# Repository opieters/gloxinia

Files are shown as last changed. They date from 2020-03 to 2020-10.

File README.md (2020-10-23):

Gloxinia
========

Open-source release of code and PCB-design files of the Gloxinia platform.

Building the code requires MPLAB X 1.35 or above and KiCAD 5.0.2 or above. 

Citing
------

If you use this code for a scientific publication, please consider citing our paper [_Gloxinia—An Open-Source Sensing Platform to Monitor the Dynamic Responses of Plants_](https://doi.org/10.3390/s20113055).

Licence
-------

GNU GPLv3 4.0

A copy of the licence can be found in `LICENCE`.

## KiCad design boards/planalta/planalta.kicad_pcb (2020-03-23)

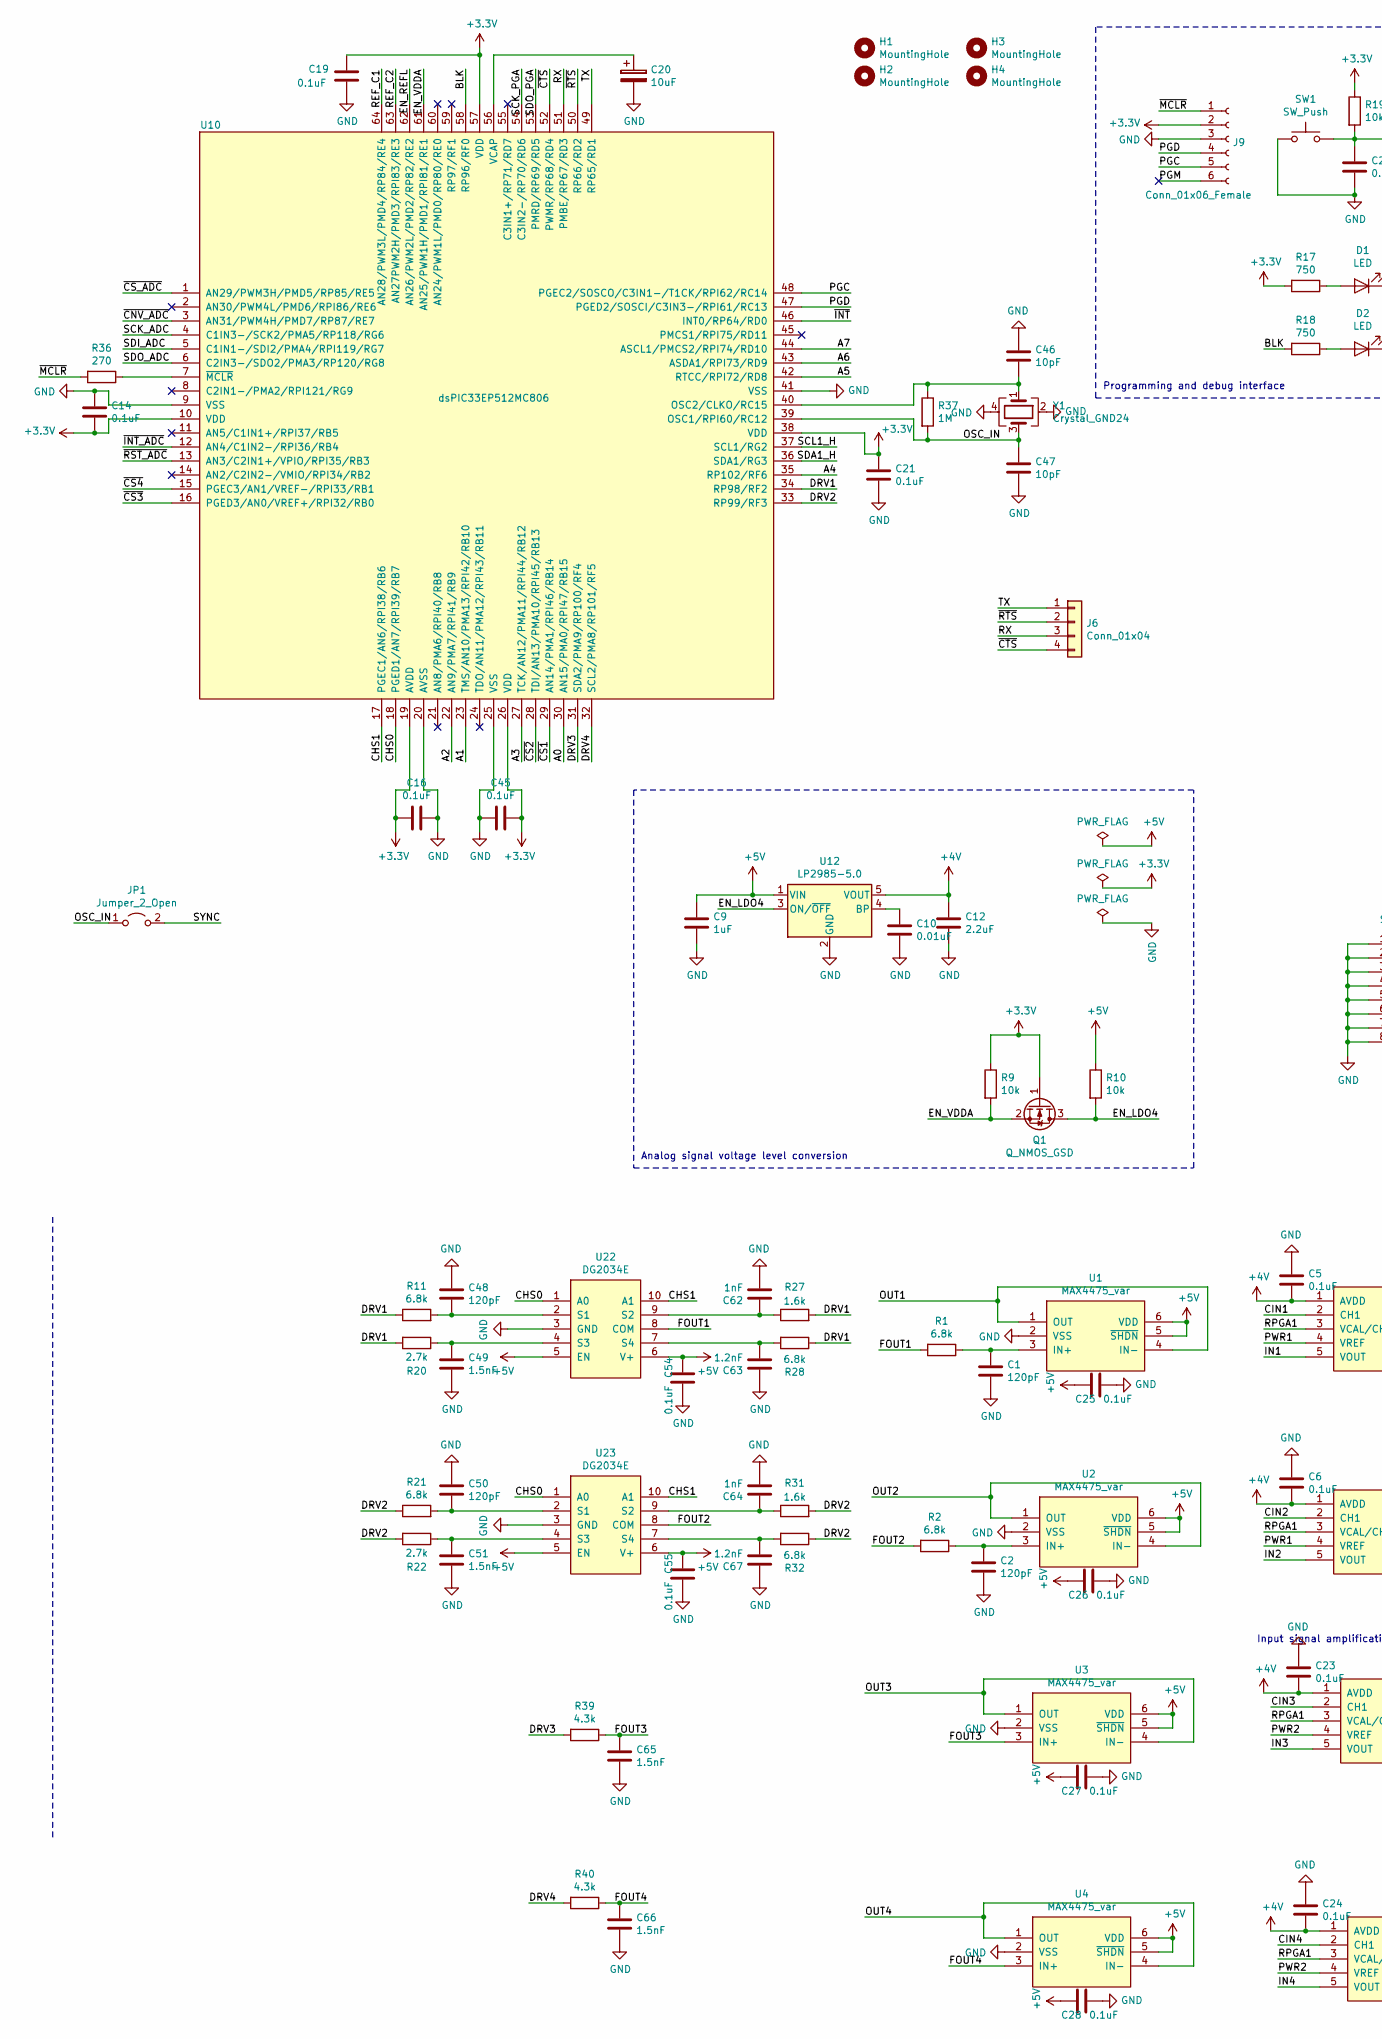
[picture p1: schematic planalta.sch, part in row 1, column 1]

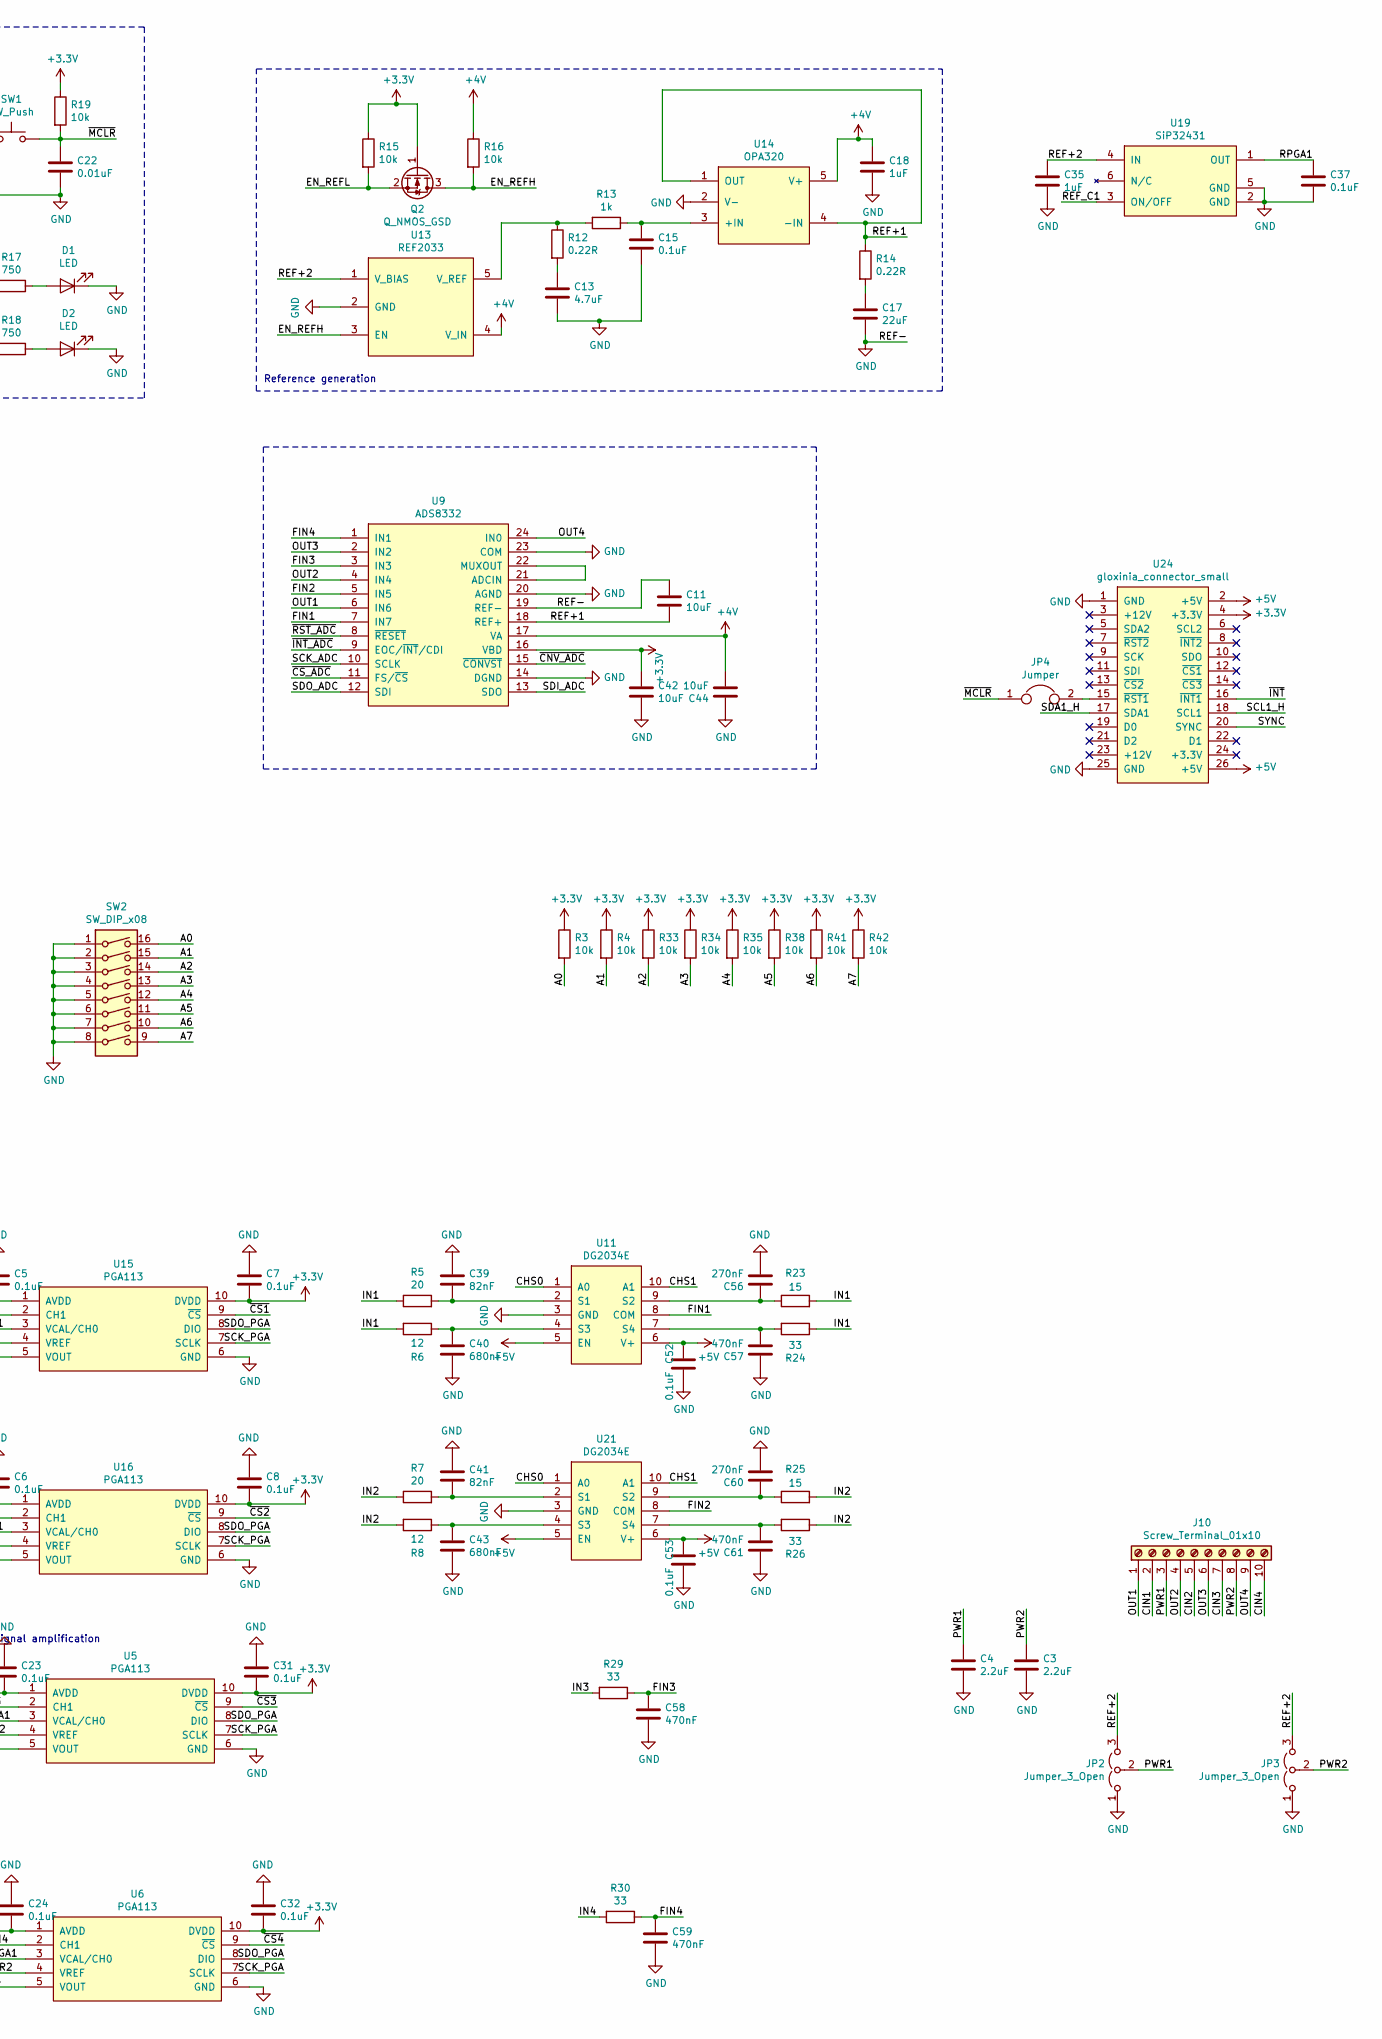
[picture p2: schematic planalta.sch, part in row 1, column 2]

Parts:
C1, C2, C48, C50: 120pF; C_0603_1608Metric; Mouser 80-C0603C121J5GAC
C3, C4, C12: 2.2uF; C_1206_3216Metric; Mouser 791-1206X225K250CT
C5, C6, C7, C8, C14, C15, C16, C19, C21, C23, C24, C25, C26, C27, C28, C31, C32, C37, C45, C52, C53, C54, C55: 0.1uF; C_0603_1608Metric; Mouser 710-885012206071
C9, C18, C35: 1uF; C_0603_1608Metric; Mouser 81-GCM188R71C105K64D
C10, C22: 0.01uF; C_0603_1608Metric; Mouser 81-GRM033C81E103KE4E
C11, C20, C42, C44: 10uF; C_1210_3225Metric; Mouser 963-TMK325BJ106KM-P
C13: 4.7uF; C_1206_3216Metric; Mouser 81-GCG31CR71E475JA1L
C17: 22uF; C_1206_3216Metric; Mouser 963-TMK316BBJ226ML-T
C39, C41: 82nF; C_0603_1608Metric; Mouser 80-C0603C823J3R
C40, C43: 680nF; C_0603_1608Metric; Mouser 710-885012206051
C46, C47: 10pF; C_0603_1608Metric; Mouser 603-CC603FRNPO9BN100
C49, C51, C65, C66: 1.5nF; C_0603_1608Metric; Mouser 710-885012206035
C56, C60: 270nF; C_0603_1608Metric; Mouser 80-C0603C274K8P
C57, C58, C59, C61: 470nF; C_0603_1608Metric; Mouser 710-885012206075
C62, C64: 1nF; C_0603_1608Metric; Mouser 963-TMK325B7105KD-T
C63, C67: 1.2nF; C_0603_1608Metric; Mouser 81-GRM1885C1H122JA01
D1, D2: LED; LED_0603_1608Metric; Mouser 78-TLMS1000
H1, H2, H3, H4: MountingHole; MountingHole_3.2mm_M3
J6: Conn_01x04; PinHeader_1x04_P2.54mm_Vertical
J9: Conn_01x06_Female; PinSocket_1x06_P2.54mm_Vertical
J10: Screw_Terminal_01x10; Header-P5.00mm-10C; Mouser TB003-500-P10BE
JP1: Jumper_2_Open; SolderJumper-2_P1.3mm_Open_Pad1.0x1.5mm
JP2, JP3: Jumper_3_Open; SolderJumper-3_P1.3mm_Open_RoundedPad1.0x1.5mm
JP4: Jumper; SolderJumper-2_P1.3mm_Open_RoundedPad1.0x1.5mm
Q1, Q2: Q_NMOS_GSD; SOT-23; Mouser 512-BSS138
R1, R2, R11, R21, R28, R32: 6.8k; R_0603_1608Metric; Mouser 667-ERJ-3RBD6801V
R3, R4, R9, R10, R15, R16, R19, R33, R34, R35, R38, R41, R42: 10k; R_0603_1608Metric; Mouser 284-APC0603B10K0N
R5, R7: 20; R_0603_1608Metric; Mouser 71-CRCW060320R0FKEAC
R6, R8: 12; R_0603_1608Metric; Mouser 667-ERJ-3EKF15R0V
R12, R14: 0.22R; R_0603_1608Metric; Mouser 667-ERJ-3RQFR22V
R13: 1k; R_0603_1608Metric; Mouser 652-CR0603-FX1001HLF
R17, R18: 750; R_0603_1608Metric; Mouser 603-RC0603FR-07750RL
R20, R22: 2.7k; R_0603_1608Metric; Mouser 603-AC0603FR-102K7L
R23, R25: 15; R_0603_1608Metric; Mouser 667-ERJ-3EKF15R0V
R24, R26, R29, R30: 33; R_0603_1608Metric; Mouser 71-CRCW060333R0FKEAC
R27, R31: 1.6k; R_0603_1608Metric; Mouser 603-RC0603FR-071K6L
R36: 270; R_0603_1608Metric; Mouser 603-RC0603FR-07270RL
R37: 1M; R_0603_1608Metric; Mouser 603-RC0603FR-101ML
R39, R40: 4.3k; R_0603_1608Metric
SW1: SW_Push; SW_SPST_KMR2; Mouser 611-KMR621NGLFS
SW2: SW_DIP_x08; SW_DIP_SPSTx08_Slide_Omron_A6H-8101_W6.15mm_P1.27mm; Mouser 653-A6H-8101
U1, U2, U3, U4: MAX4475_var; SOT-23-6; Mouser 700-MAX4475AUT+T
U5, U6, U15, U16: PGA113; MSOP-10_3x3mm_P0.5mm; Mouser 595-PGA113AIDGSR
U9: ADS8332; TSSOP-24_4.4x7.8mm_P0.65mm; Mouser 595-ADS8332IBPWR
U10: dsPIC33EP512MC806; TQFP-64_10x10mm_P0.5mm; Mouser 579-33EP512MC806IPT
U11, U21, U22, U23: DG2034E; MSOP-10_3x3mm_P0.5mm; Mouser 78-DG2034EDQ-T1-GE3
U12: LP2985-5.0; SOT-23-5; Mouser 926-LP2985IM540NOPB
U13: REF2033; SOT-23-5; Mouser 595-REF2033AIDDCR
U14: OPA320; SOT-23-5; Mouser 595-OPA320AIDBVR
U19: SiP32431; SOT-363_SC-70-6; Mouser 781-SIP32431DR3-GE3
U24: gloxinia_connector_small; PinHeader_2x13_P2.54mm_Vertical; Mouser 200-SSQ11303TD
Y1: Crystal_GND24; Crystal_SMD_Abracon_ABM3B-4Pin_5.0x3.2mm; Mouser 520-80-10-30B-CWNT

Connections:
+3V3: C7.2, C8.2, C14.2, C16.2, C19.1, C21.1, C31.2, C32.2, C42.1, C45.1, J9.2, Q1.1 (G), Q2.1 (G), R3.1, R4.1, R9.1, R15.1, R17.2, R19.1, R33.1, R34.1, R35.1, R38.1, R41.1, R42.1, U5.10 (DVDD), U6.10 (DVDD), U9.16 (VBD), U10.10 (VDD), U10.19 (AVDD), U10.26 (VDD), U10.38 (VDD), U10.57 (VDD), U15.10 (DVDD), U16.10 (DVDD), U24.4 (+3.3V)
+4V: C5.2, C6.2, C12.1, C18.1, C23.2, C24.2, C44.2, R16.1, U5.1 (AVDD), U6.1 (AVDD), U9.17 (VA), U12.5 (VOUT), U13.4 (V_IN), U14.5 (V+), U15.1 (AVDD), U16.1 (AVDD)
+5V: C9.1, C25.2, C26.2, C27.2, C28.2, C52.2, C53.2, C54.2, C55.2, R10.1, U1.5 (~SHDN), U1.6 (VDD), U2.5 (~SHDN), U2.6 (VDD), U3.5 (~SHDN), U3.6 (VDD), U4.5 (~SHDN), U4.6 (VDD), U11.5 (EN), U11.6 (V+), U12.1 (VIN), U21.5 (EN), U21.6 (V+), U22.5 (EN), U22.6 (V+), U23.5 (EN), U23.6 (V+), U24.2 (+5V), U24.26 (+5V)
/A0: R3.2, SW2.16, U10.30 (AN15/PMA0/RPI47/RB15)
/A1: R4.2, SW2.15, U10.23 (TMS/AN10/PMA13/RPI42/RB10)
/A2: R33.2, SW2.14, U10.22 (AN9/PMA7/RPI41/RB9)
/A3: R34.2, SW2.13, U10.27 (TCK/AN12/PMA11/RPI44/RB12)
/A4: R35.2, SW2.12, U10.35 (RP102/RF6)
/A5: R38.2, SW2.11, U10.42 (RTCC/RPI72/RD8)
/A6: R41.2, SW2.10, U10.43 (ASDA1/RPI73/RD9)
/A7: R42.2, SW2.9, U10.44 (ASCL1/PMCS2/RPI74/RD10)
/BLK: R18.2, U10.58 (RP96/RF0)
/CHS0: U10.18 (PGED1/AN7/RPI39/RB7), U11.1 (A0), U21.1 (A0), U22.1 (A0), U23.1 (A0)
/CHS1: U10.17 (PGEC1/AN6/RPI38/RB6), U11.10 (A1), U21.10 (A1), U22.10 (A1), U23.10 (A1)
/CIN1: J10.2, U15.2 (CH1)
/CIN2: J10.5, U16.2 (CH1)
/CIN3: J10.7, U5.2 (CH1)
/CIN4: J10.10, U6.2 (CH1)
/DRV1: R11.1, R20.2, R27.2, R28.1, U10.34 (RP98/RF2)
/DRV2: R21.1, R22.2, R31.2, R32.1, U10.33 (RP99/RF3)
/DRV3: R39.2, U10.31 (SDA2/PMA9/RP100/RF4)
/DRV4: R40.2, U10.32 (SCL2/PMA8/RP101/RF5)
/EN_LDO4: Q1.3 (D), R10.2, U12.3 (ON/~OFF~)
/EN_REFH: Q2.3 (D), R16.2, U13.3 (EN)
/EN_REFL: Q2.2 (S), R15.2, U10.62 (AN26/PWM2L/PMD2/RP82/RE2)
/EN_VDDA: Q1.2 (S), R9.2, U10.61 (AN25/PWM1H/PMD1/RPI81/RE1)
/FIN1: U9.7 (IN7), U11.8 (COM)
/FIN2: U9.5 (IN5), U21.8 (COM)
/FIN3: C58.1, R29.1, U9.3 (IN3)
/FIN4: C59.1, R30.1, U9.1 (IN1)
/FOUT1: R1.2, U22.8 (COM)
/FOUT2: R2.2, U23.8 (COM)
/FOUT3: C65.1, R39.1, U3.3 (IN+)
/FOUT4: C66.1, R40.1, U4.3 (IN+)
/IN1: R5.1, R6.2, R23.2, R24.1, U15.5 (VOUT)
/IN2: R7.1, R8.2, R25.2, R26.1, U16.5 (VOUT)
/IN3: R29.2, U5.5 (VOUT)
/IN4: R30.2, U6.5 (VOUT)
/OSC_IN: C47.1, JP1.1 (A), R37.2, U10.39 (OSC1/RPI60/RC12), Y1.3
/OUT1: J10.1, U1.1 (OUT), U1.4 (IN-), U9.6 (IN6)
/OUT2: J10.4, U2.1 (OUT), U2.4 (IN-), U9.4 (IN4)
/OUT3: J10.6, U3.1 (OUT), U3.4 (IN-), U9.2 (IN2)
/OUT4: J10.9, U4.1 (OUT), U4.4 (IN-), U9.24 (IN0)
/PGC: J9.5, U10.48 (PGEC2/SOSCO/C3IN1-/T1CK/RPI62/RC14)
/PGD: J9.4, U10.47 (PGED2/SOSCI/C3IN3-/RPI61/RC13)
/PGM: J9.6
/PWR1: C4.1, J10.3, JP2.2 (C), U15.4 (VREF), U16.4 (VREF)
/PWR2: C3.1, J10.8, JP3.2 (C), U5.4 (VREF), U6.4 (VREF)
/REF+1: C11.2, R14.1, U9.18 (REF+), U14.1 (OUT), U14.4 (-IN)
/REF+2: C35.1, JP2.3 (B), JP3.3 (B), U13.1 (V_BIAS), U19.4 (IN)
/REF_C1: U10.64 (AN28/PWM3L/PMD4/RP84/RE4), U19.3 (ON/OFF)
/REF_C2: U10.63 (AN27PWM2H/PMD3/RPI83/RE3)
/RPGA1: C37.1, U5.3 (VCAL/CH0), U6.3 (VCAL/CH0), U15.3 (VCAL/CH0), U16.3 (VCAL/CH0), U19.1 (OUT)
/RX: J6.3, U10.51 (PMBE/RP67/RD3)
/SCK_ADC: U9.10 (SCLK), U10.4 (C1IN3-/SCK2/PMA5/RP118/RG6)
/SCK_PGA: U5.7 (SCLK), U6.7 (SCLK), U10.54 (C3IN2-/RP70/RD6), U15.7 (SCLK), U16.7 (SCLK)
/SCL1_H: U10.37 (SCL1/RG2), U24.18 (SCL1)
/SDA1_H: U10.36 (SDA1/RG3), U24.17 (SDA1)
/SDI_ADC: U9.13 (SDO), U10.5 (C1IN1-/SDI2/PMA4/RPI119/RG7)
/SDO_ADC: U9.12 (SDI), U10.6 (C2IN3-/SDO2/PMA3/RP120/RG8)
/SDO_PGA: U5.8 (DIO), U6.8 (DIO), U10.53 (PMRD/RP69/RD5), U15.8 (DIO), U16.8 (DIO)
/SYNC: JP1.2 (B), U24.20 (SYNC)
/TX: J6.1, U10.49 (RP65/RD1)
/~CNV_ADC: U9.15 (~CONVST), U10.3 (AN31/PWM4H/PMD7/RP87/RE7)
/~CS1: U10.29 (AN14/PMA1/RPI46/RB14), U15.9 (~CS)
/~CS2: U10.28 (TDI/AN13/PMA10/RPI45/RB13), U16.9 (~CS)
/~CS3: U5.9 (~CS), U10.16 (PGED3/AN0/VREF+/RPI32/RB0)
/~CS4: U6.9 (~CS), U10.15 (PGEC3/AN1/VREF-/RPI33/RB1)
/~CS_ADC: U9.11 (FS/~CS), U10.1 (AN29/PWM3H/PMD5/RP85/RE5)
/~CTS: J6.4, U10.52 (PWMR/RP68/RD4)
/~INT: U10.46 (INT0/RP64/RD0), U24.16 (~INT1)
/~INT_ADC: U9.9 (EOC/~INT~/CDI), U10.12 (AN4/C1IN2-/RPI36/RB4)
/~MCLR: C22.1, J9.1, JP4.1, R19.2, R36.2, SW1.2
/~RST_ADC: U9.8 (~RESET), U10.13 (AN3/C2IN1+/VPIO/RPI35/RB3)
/~RTS: J6.2, U10.50 (RP66/RD2)
GND: C1.2, C2.2, C3.2, C4.2, C5.1, C6.1, C7.1, C8.1, C9.2, C10.2, C11.1, C12.2, C13.2, C14.1, C15.2, C16.1, C17.2, C18.2, C19.2, C20.2, C21.2, C22.2, C23.1, C24.1, C25.1, C26.1, C27.1, C28.1, C31.1, C32.1, C35.2, C37.2, C39.1, C40.2, C41.1, C42.2, C43.2, C44.1, C45.2, C46.1, C47.2, C48.1, C49.2, C50.1, C51.2, C52.1, C53.1, C54.1, C55.1, C56.2, C57.1, C58.2, C59.2, C60.2, C61.1, C62.2, C63.1, C64.2, C65.2, C66.2, C67.1, D1.1 (K), D2.1 (K), J9.3, JP2.1 (A), JP3.1 (A), SW1.1, SW2.1, SW2.2, SW2.3, SW2.4, SW2.5, SW2.6, SW2.7, SW2.8, U1.2 (VSS), U2.2 (VSS), U3.2 (VSS), U4.2 (VSS), U5.6 (GND), U6.6 (GND), U9.14 (DGND), U9.19 (REF-), U9.20 (AGND), U9.23 (COM), U10.9 (VSS), U10.20 (AVSS), U10.25 (VSS), U10.41 (VSS), U11.3 (GND), U12.2 (GND), U13.2 (GND), U14.2 (V-), U15.6 (GND), U16.6 (GND), U19.2 (GND), U19.5 (GND), U21.3 (GND), U22.3 (GND), U23.3 (GND), U24.1 (GND), U24.25 (GND), Y1.2, Y1.4
unnamed: C1.1, R1.1, U1.3 (IN+)
unnamed: C2.1, R2.1, U2.3 (IN+)
unnamed: C10.1, U12.4 (BP)
unnamed: C13.1, R12.2
unnamed: C15.1, R13.1, U14.3 (+IN)
unnamed: C17.1, R14.2
unnamed: C20.1, U10.56 (VCAP)
unnamed: C39.2, R5.2, U11.2 (S1)
unnamed: C40.1, R6.1, U11.4 (S3)
unnamed: C41.2, R7.2, U21.2 (S1)
unnamed: C43.1, R8.1, U21.4 (S3)
unnamed: C46.2, R37.1, U10.40 (OSC2/CLKO/RC15), Y1.1
unnamed: C48.2, R11.2, U22.2 (S1)
unnamed: C49.1, R20.1, U22.4 (S3)
unnamed: C50.2, R21.2, U23.2 (S1)
unnamed: C51.1, R22.1, U23.4 (S3)
unnamed: C56.1, R23.1, U11.9 (S2)
unnamed: C57.2, R24.2, U11.7 (S4)
unnamed: C60.1, R25.1, U21.9 (S2)
unnamed: C61.2, R26.2, U21.7 (S4)
unnamed: C62.1, R27.1, U22.9 (S2)
unnamed: C63.2, R28.2, U22.7 (S4)
unnamed: C64.1, R31.1, U23.9 (S2)
unnamed: C67.2, R32.2, U23.7 (S4)
unnamed: D1.2 (A), R17.1
unnamed: D2.2 (A), R18.1
unnamed: JP4.2, U24.15 (~RST1)
unnamed: R12.1, R13.2, U13.5 (V_REF)
unnamed: R36.1, U10.7 (~MCLR)
unnamed: U9.21 (ADCIN), U9.22 (MUXOUT)

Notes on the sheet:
Programming and debug interface
Reference generation
Analog signal voltage level conversion
Input signal amplification

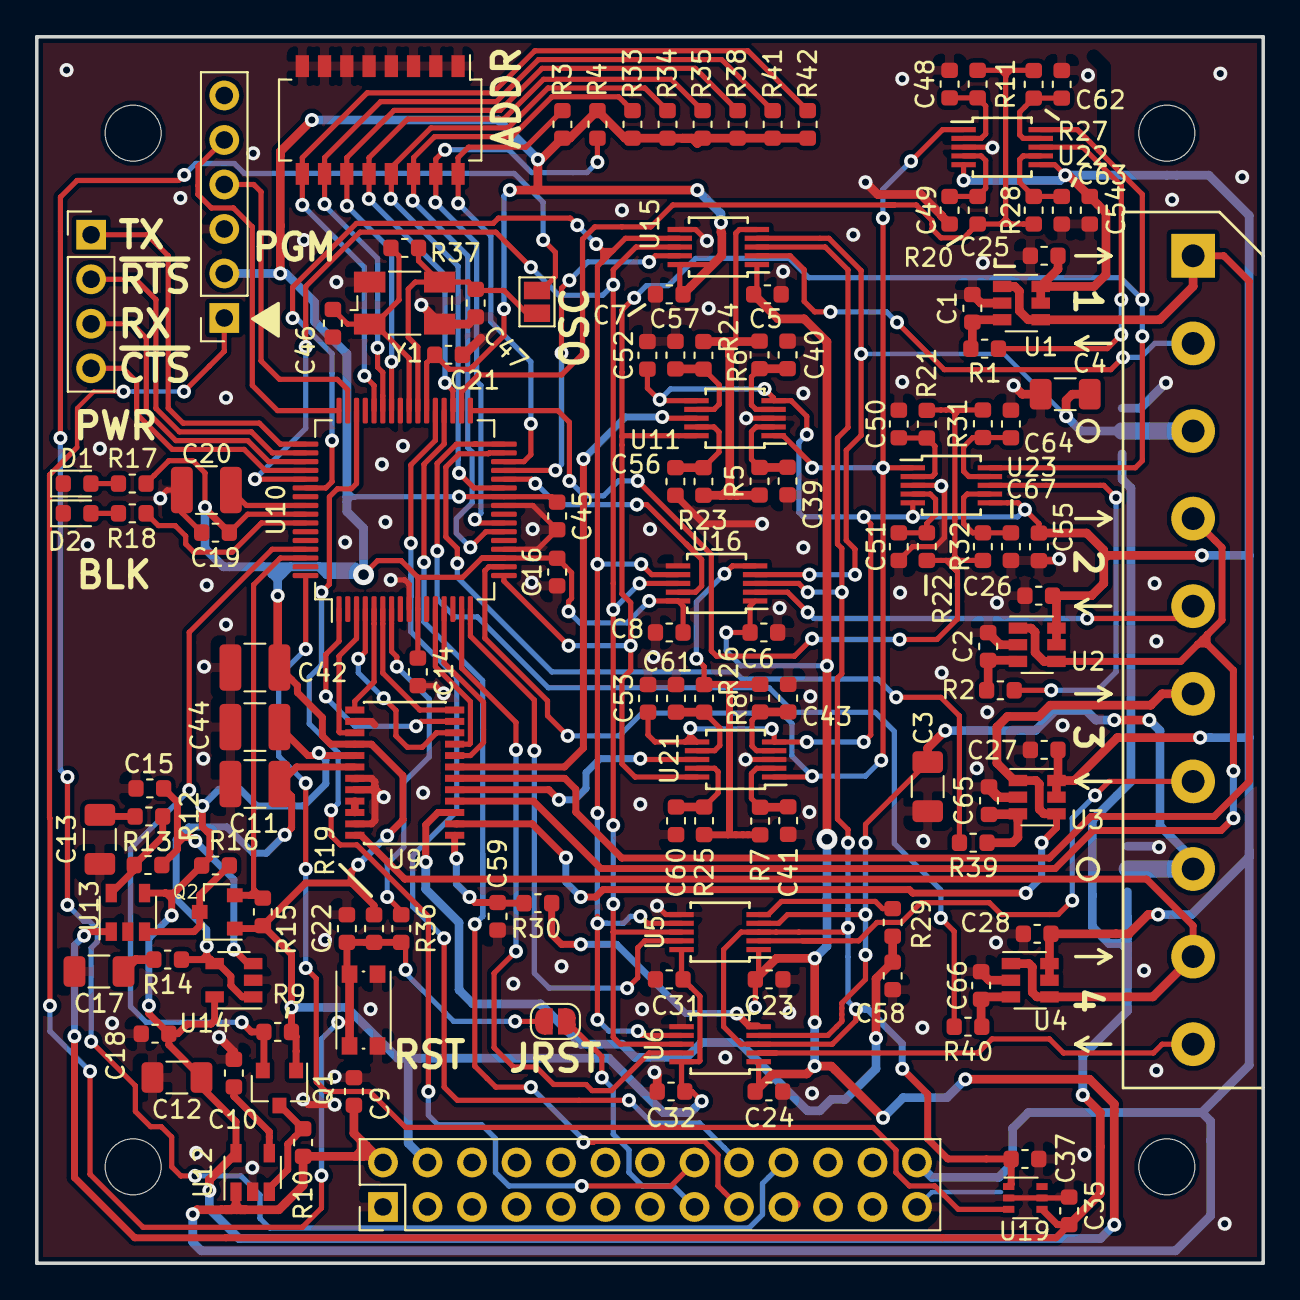
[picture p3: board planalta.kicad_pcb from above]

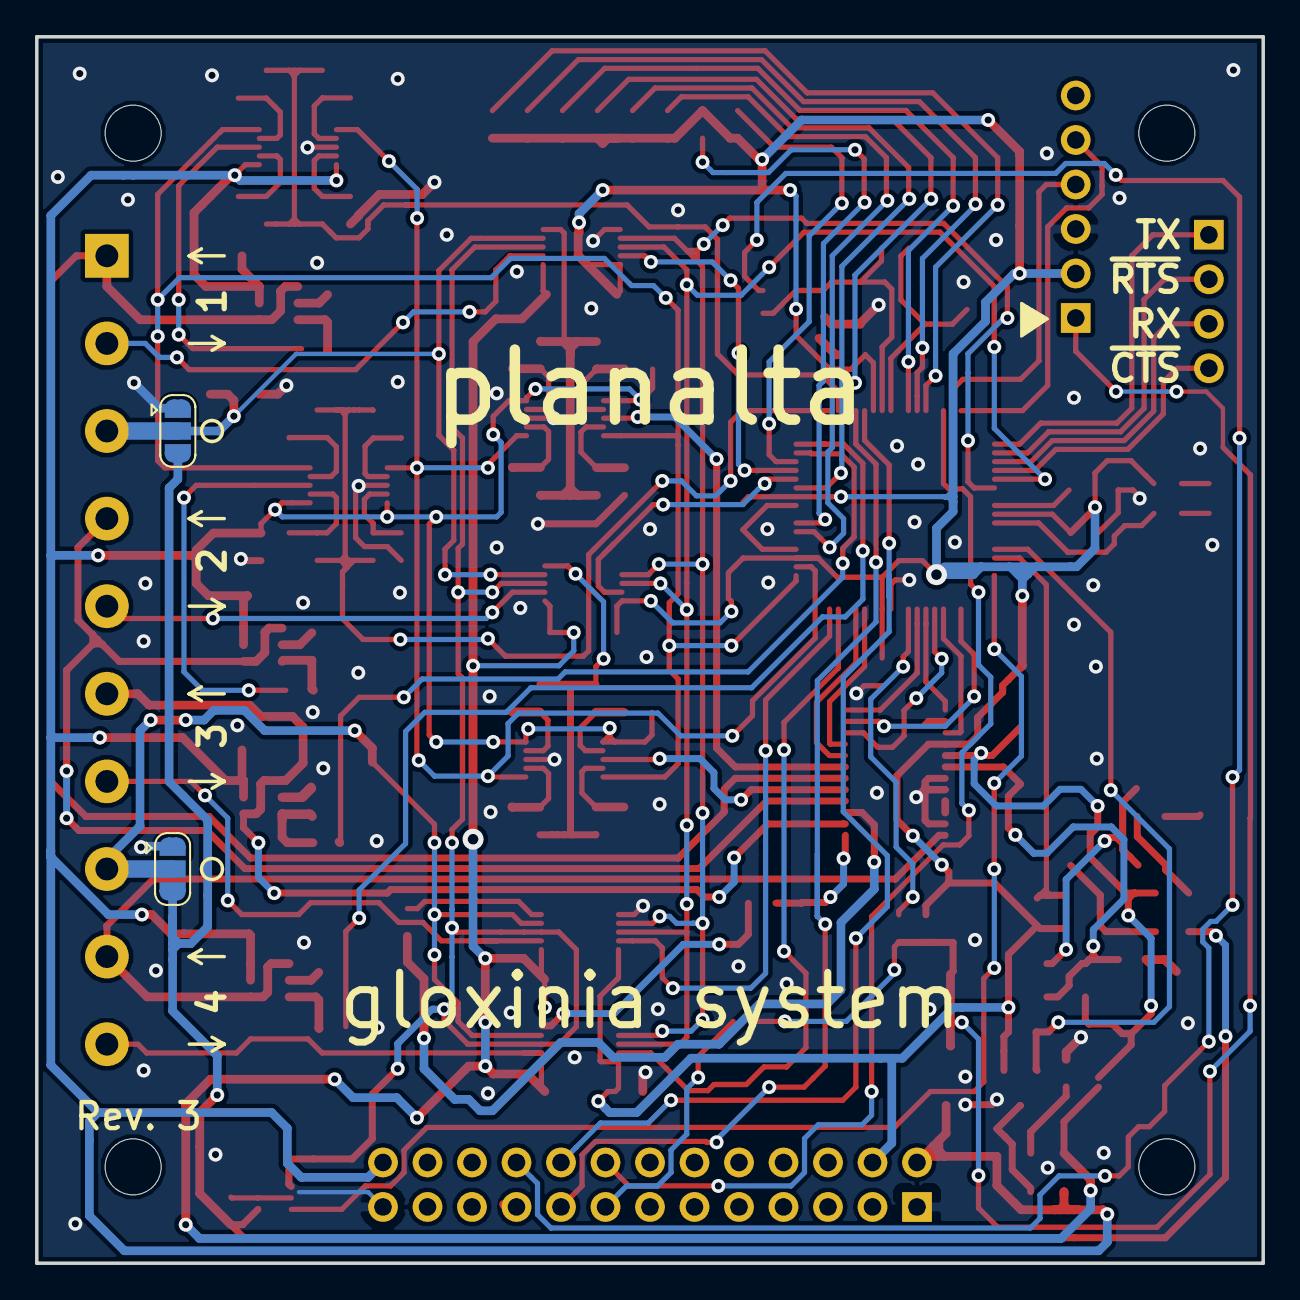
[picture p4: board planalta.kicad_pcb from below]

Board: 2 copper layers, 70.0 x 70.0 mm, 140 parts (2 on the bottom side), 104 nets.

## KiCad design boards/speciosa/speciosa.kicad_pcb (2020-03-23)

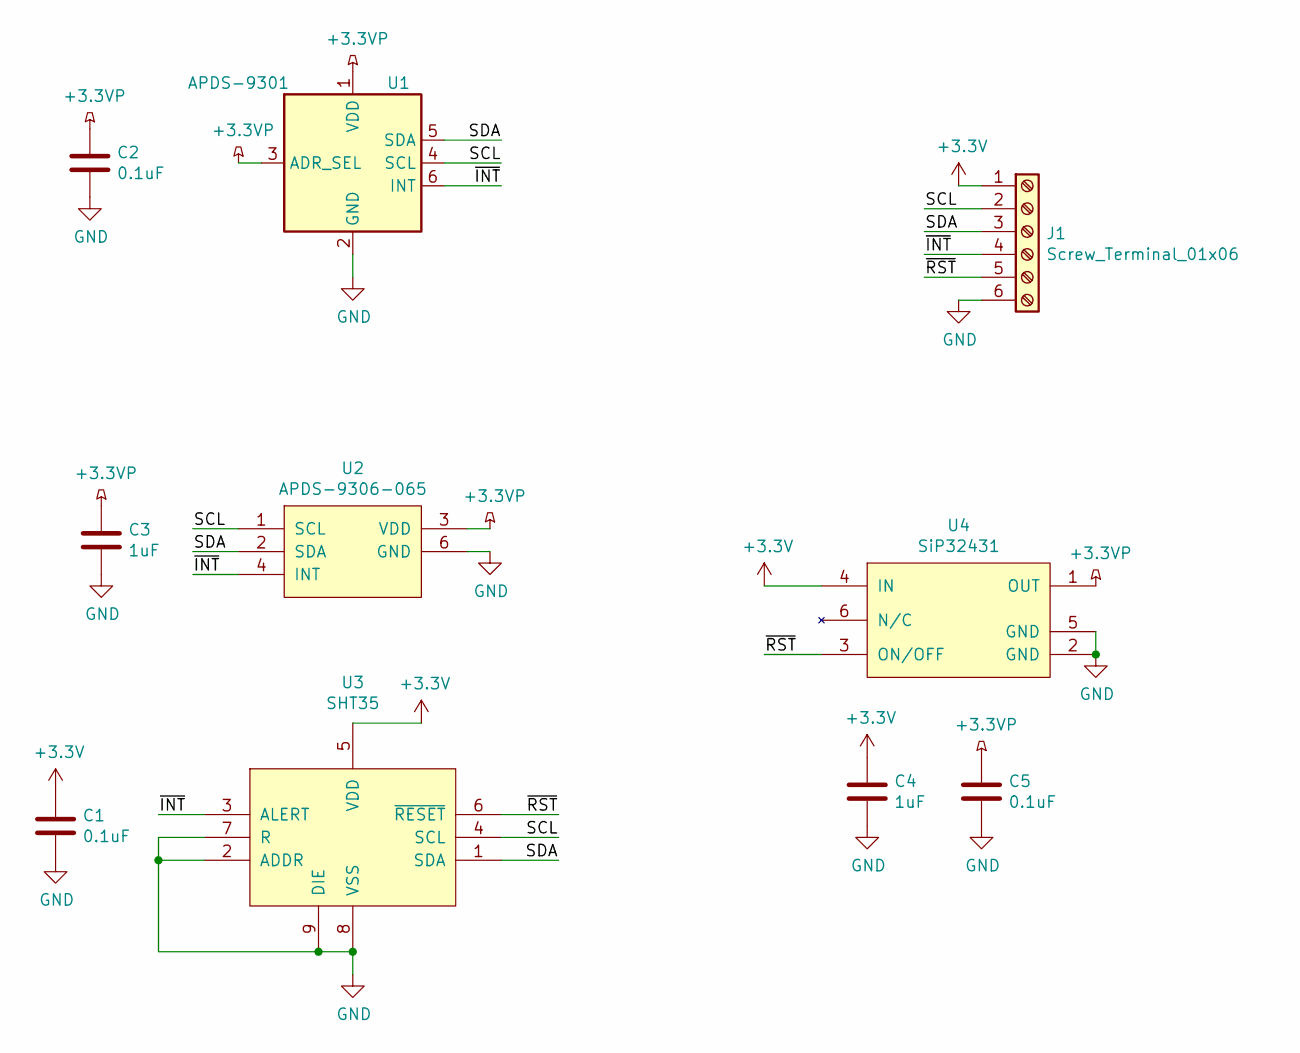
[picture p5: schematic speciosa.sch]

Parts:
C1, C2, C5: 0.1uF; C_0603_1608Metric; Mouser 810-CGA3E2X8R1E104K
C3, C4: 1uF; C_0603_1608Metric; Mouser 710-885012106022
J1: Screw_Terminal_01x06; PinHeader_1x06_P2.54mm_Vertical
U1: APDS-9301; Broadcom_APDS-9301; Farnell 2497389
U2: APDS-9306-065; Mouser 630-APDS-9306-065
U3: SHT35; 8P-1EP-DFN_2.5x2.5; Mouser 403-SHT35-DIS-F
U4: SiP32431; SOT-363_SC-70-6; Mouser 781-SIP32431DR3-GE3

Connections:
+3.3VP: C2.1, C3.1, C5.1, U1.1 (VDD), U1.3 (ADR_SEL), U2.3 (VDD), U4.1 (OUT)
+3V3: C1.1, C4.1, J1.1, U3.5 (VDD), U4.4 (IN)
/SCL: J1.2, U1.4 (SCL), U2.1 (SCL), U3.4 (SCL)
/SDA: J1.3, U1.5 (SDA), U2.2 (SDA), U3.1 (SDA)
/~INT: J1.4, U1.6 (INT), U2.4 (INT), U3.3 (ALERT)
/~RST: J1.5, U3.6 (~RESET), U4.3 (ON/OFF)
GND: C1.2, C2.2, C3.2, C4.2, C5.2, J1.6, U1.2 (GND), U2.6 (GND), U3.2 (ADDR), U3.7 (R), U3.8 (VSS), U3.9 (DIE), U4.2 (GND), U4.5 (GND)

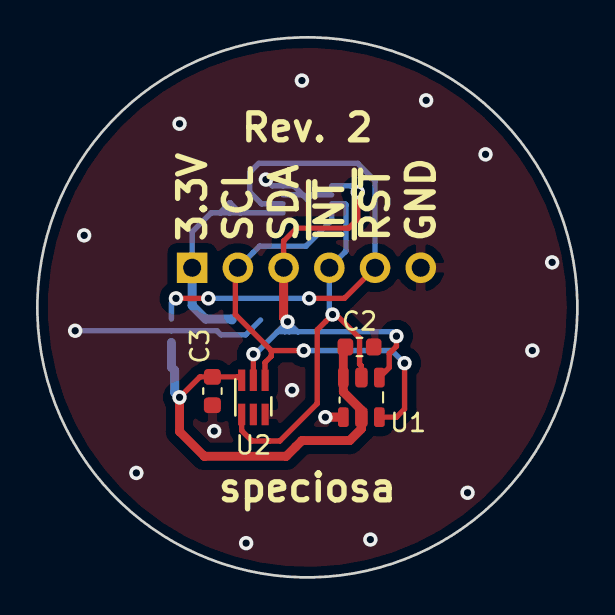
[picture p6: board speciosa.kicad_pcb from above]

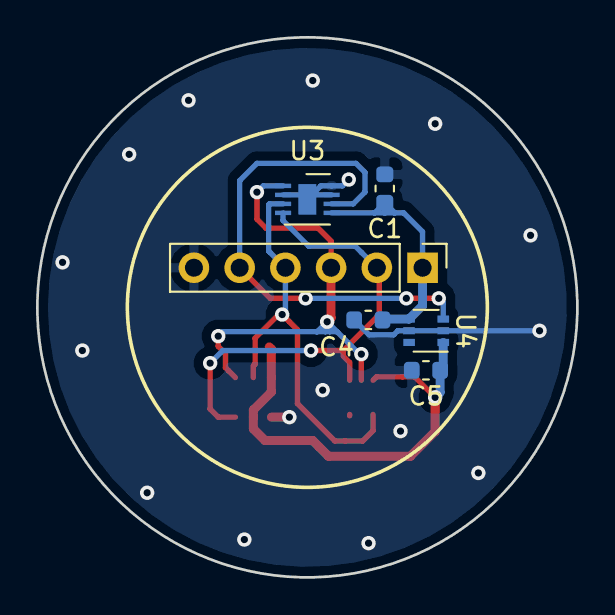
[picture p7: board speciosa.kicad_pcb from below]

Board: 2 copper layers, 30.0 x 30.0 mm, 10 parts (6 on the bottom side), 7 nets.

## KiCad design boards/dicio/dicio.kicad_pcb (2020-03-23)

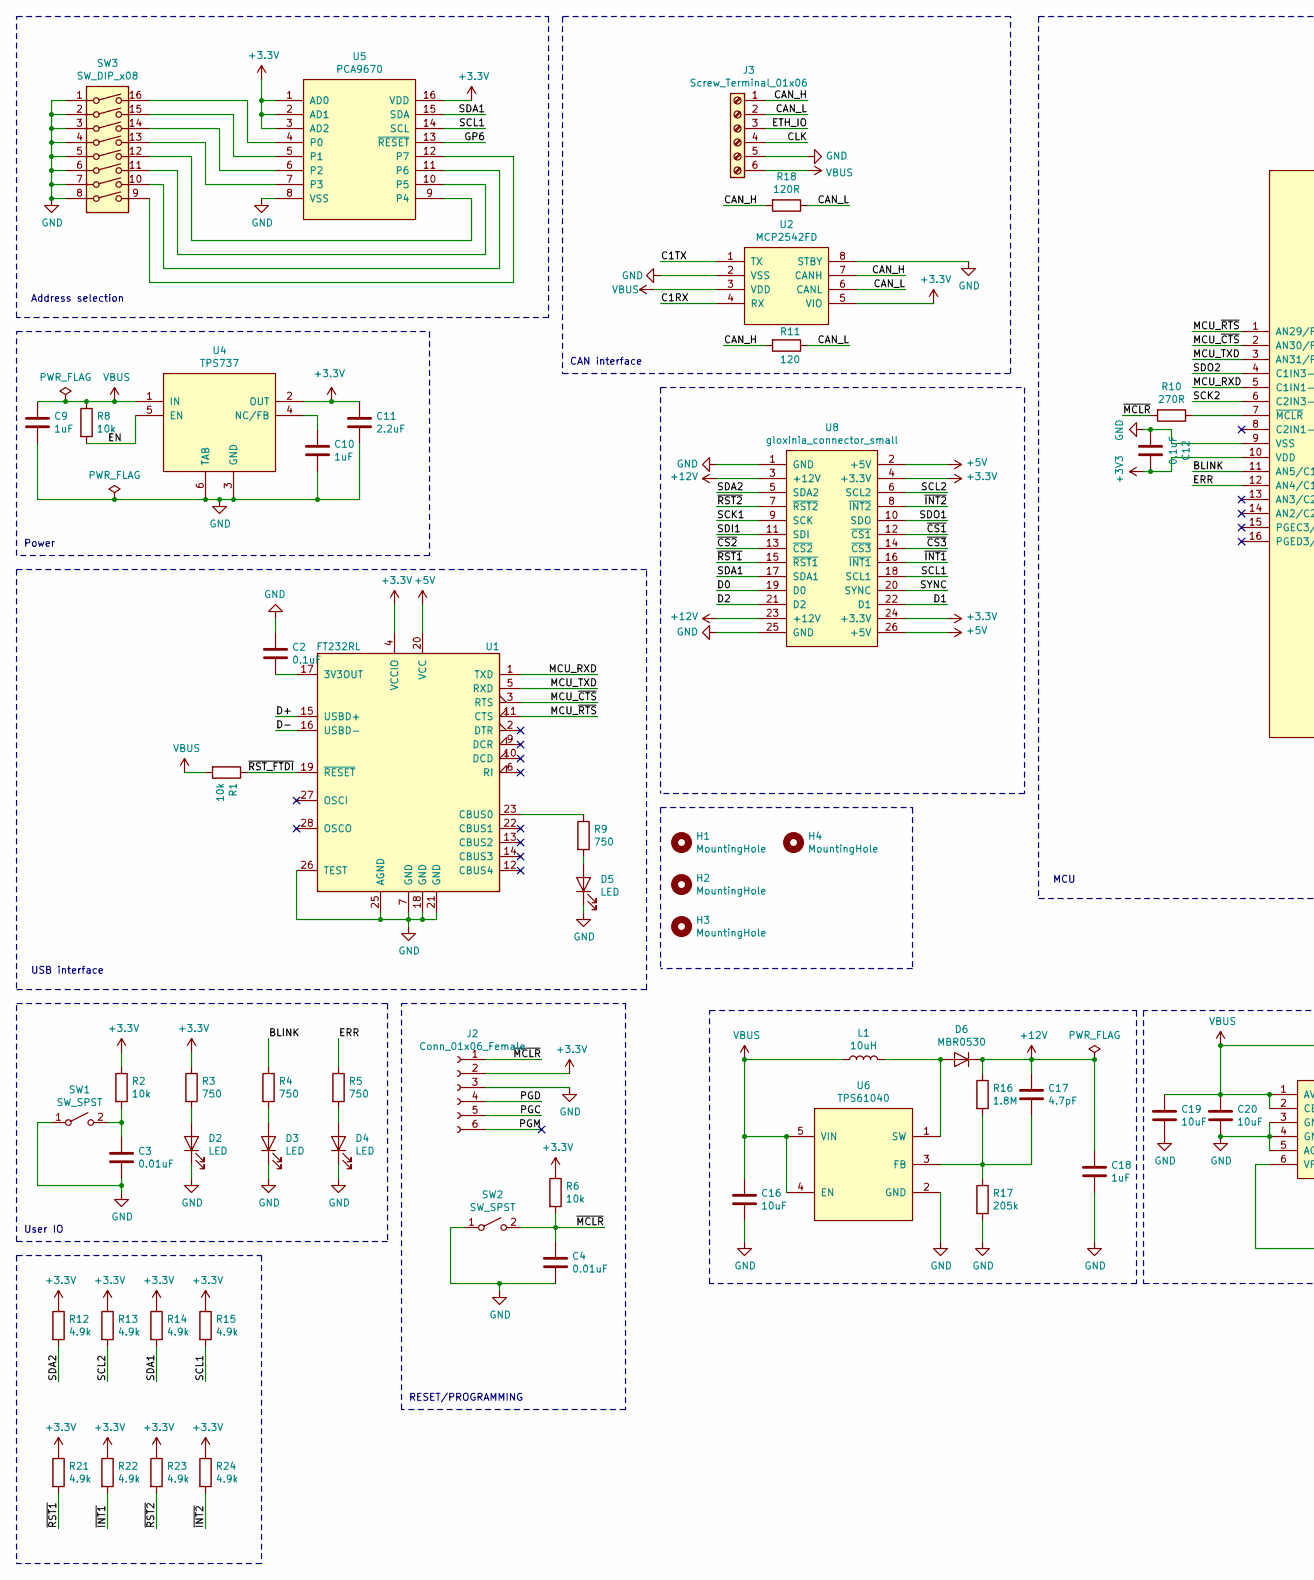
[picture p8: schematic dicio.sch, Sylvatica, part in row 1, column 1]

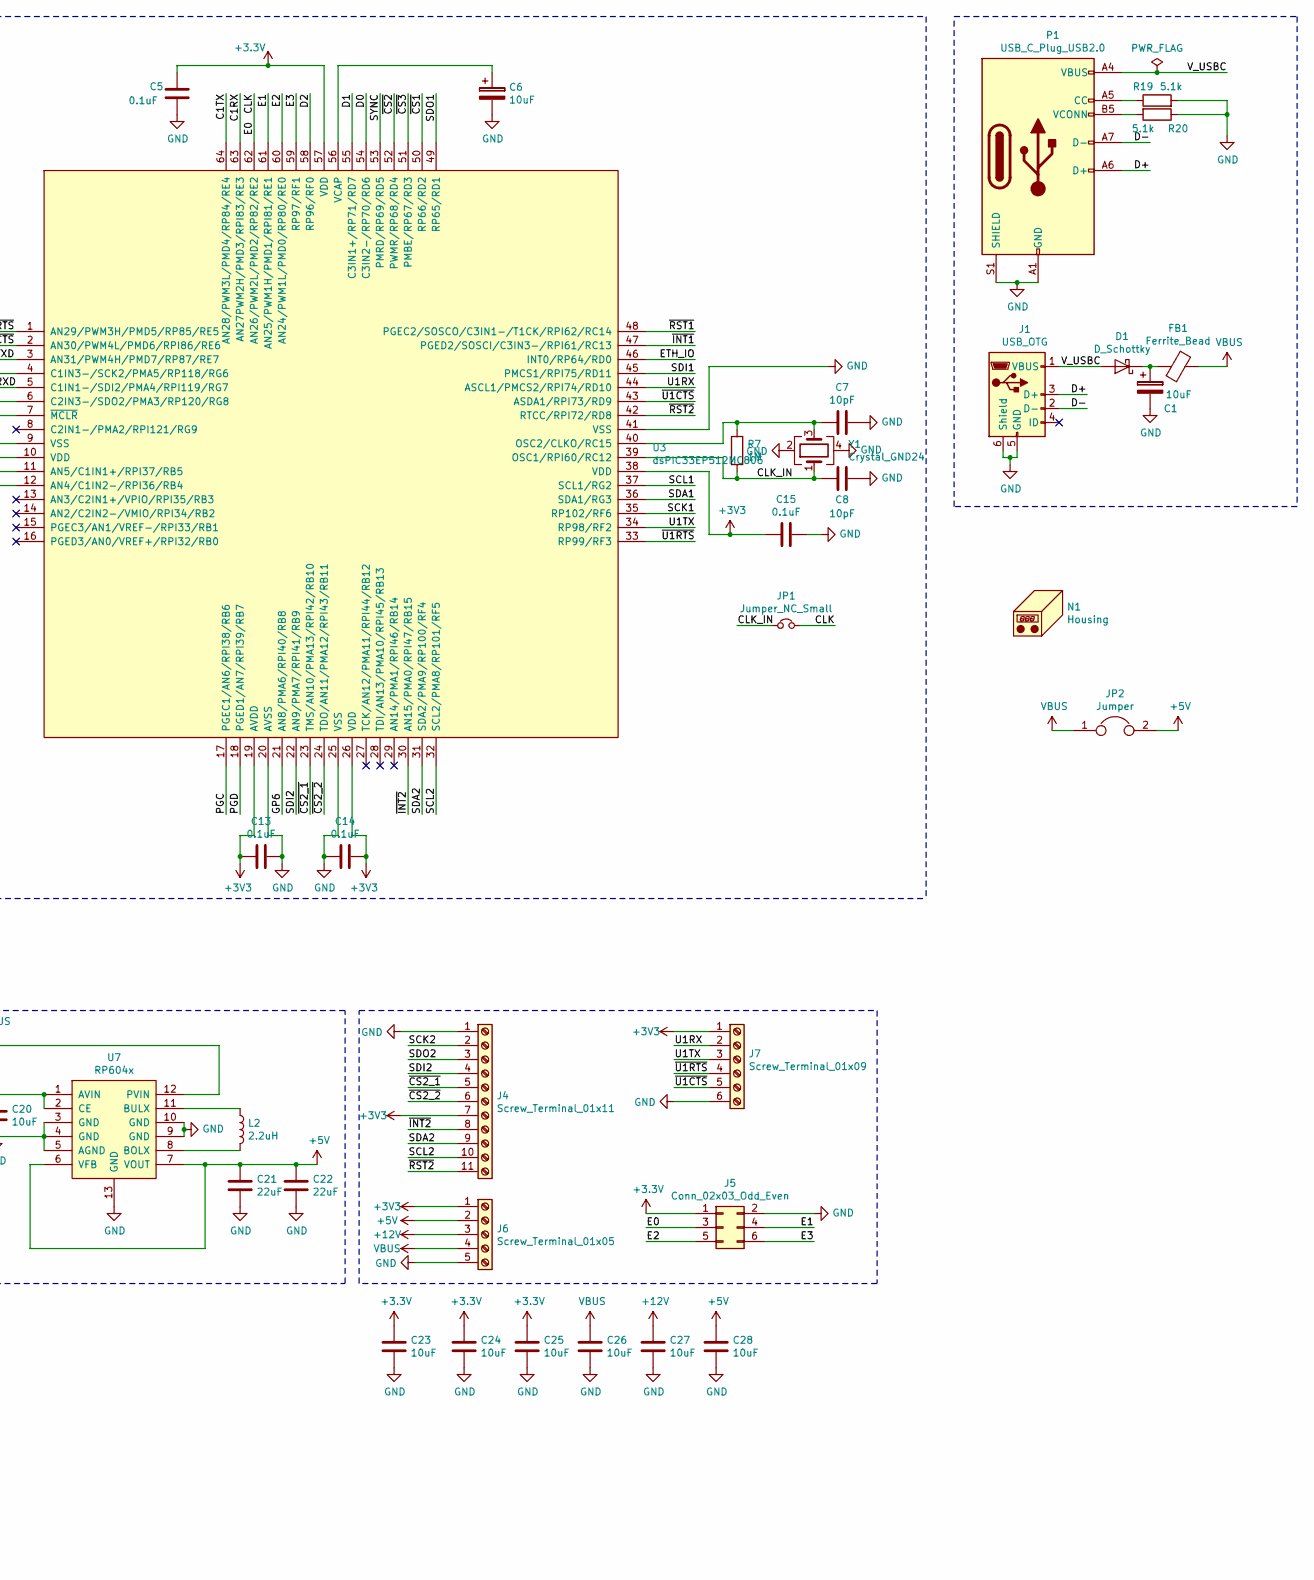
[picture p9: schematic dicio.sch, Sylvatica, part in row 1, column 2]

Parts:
C1, C6, C16, C19, C20, C23, C24, C25, C26, C27, C28: 10uF; C_1210_3225Metric; Mouser 963-TMK325BJ106KM-P
C2, C5, C12, C13, C14, C15: 0.1uF; C_0603_1608Metric; Mouser 710-885012206071
C3, C4: 0.01uF; C_0603_1608Metric; Mouser 710-885012206065
C7, C8: 10pF; C_0603_1608Metric; Mouser 603-CC603FRNPO9BN100
C9, C10, C18: 1uF; C_0603_1608Metric; Mouser 963-TMK325B7105KD-T
C11: 2.2uF; C_1206_3216Metric; Mouser 791-1206X225K250CT
C17: 4.7pF; C_0603_1608Metric; Mouser 710-885012006049
C21, C22: 22uF; C_1210_3225Metric; Mouser 963-TMK316BBJ226ML-T
D1: D_Schottky; D_SMB; Mouser 621-B340LB-F
D2, D3, D4, D5: LED; LED_0603_1608Metric; Mouser 78-TLMS1000
D6: MBR0530; D_SOD-123; Mouser 512-MBR0530
FB1: Ferrite_Bead; L_0805_2012Metric; Mouser 875-MI0805K400R-10
H1, H2, H3, H4: MountingHole; MountingHole_3.2mm_M3
J1: USB_OTG; USB_Micro-B_Molex-105017-0001; Mouser 538-105017-0001
J2: Conn_01x06_Female; PinSocket_1x06_P2.54mm_Vertical
J3: Screw_Terminal_01x06; TB003-500-06; Mouser 490-TB003-500-P06BE
J4: Screw_Terminal_01x11; TB003-500-11; Mouser 490-TB003-500-P11BE
J5: Conn_02x03_Odd_Even; PinHeader_2x03_P2.54mm_Vertical
J6: Screw_Terminal_01x05; TB003-500-05; Mouser 490-TB003-500-P05BE
J7: Screw_Terminal_01x09; TB003-500-06; Mouser 490-TB003-500-P06BE
JP1: Jumper_NC_Small; SolderJumper-2_P1.3mm_Open_RoundedPad1.0x1.5mm
JP2: Jumper; SolderJumper-2_P1.3mm_Open_RoundedPad1.0x1.5mm
L1: 10uH; L_6.5mmx4.5mm_Bourns; Mouser 652-SDR0703-100KL
L2: 2.2uH; L_L4mm_D4mm_H1.8mm; Mouser 875-TYS40182R2M-10
N1: Housing; Enclosure-Hammond-1554LA; Mouser 546-1554LA2GYCL
P1: USB_C_Plug_USB2.0; USB_C_Receptacle_Amphenol_12401832E402A; Mouser 523-12401832E402A
R1, R2, R6, R8: 10k; R_0603_1608Metric; Mouser 284-APC0603B10K0N
R3, R4, R5, R9: 750; R_0603_1608Metric; Mouser 603-RC0603FR-07750RL
R7: 1M; R_0603_1608Metric; Mouser 603-RC0603FR-101ML
R10: 270R; R_0603_1608Metric; Mouser 603-RC0603FR-07270RL
R11: 120; R_0603_1608Metric; Mouser 71-CRCW0603120RFKEAC
R12, R13, R14, R15, R21, R22, R23, R24: 4.9k; R_0603_1608Metric; Mouser 603-RC0603FR-0724K9L
R16: 1.8M; C_0603_1608Metric; Mouser 603-AC0603FR-071M8L
R17: 205k; C_0603_1608Metric; Mouser 603-RC0603FR-07205KL
R18: 120R; R_Axial_DIN0204_L3.6mm_D1.6mm_P7.62mm_Horizontal; Mouser 594-5063JD120R0F
R19, R20: 5.1k; R_0603_1608Metric; Mouser 603-AC0603FR-135K1L
SW1, SW2: SW_SPST; SW_SPST_KMR2; Mouser 611-KMR621NGLFS
SW3: SW_DIP_x08; SW_DIP_SPSTx08_Slide_Omron_A6H-8101_W6.15mm_P1.27mm; Mouser 653-A6H-8101
U1: FT232RL; SSOP-28_5.3x10.2mm_P0.65mm; Mouser 895-FT232RL
U2: MCP2542FD; SOIC-8_3.9x4.9mm_P1.27mm; Mouser 579-MCP2542FDT-E/SN
U3: dsPIC33EP512MC806; TQFP-64_10x10mm_P0.5mm; Mouser 579-33EP512MC806IPT
U4: TPS737; SOT-223-6; Mouser 595-TPS73733DCQR
U5: PCA9670; TSSOP-16_4.4x5mm_P0.65mm; Mouser 771-PCA9670PW118
U6: TPS61040; SOT-23-5; Mouser 595-TPS61040DBVR
U7: RP604x; DFN_12_Pin_2.7x3mm_P0.5mm; Mouser 848-RP604K501A-TR
U8: gloxinia_connector_small; PinHeader_2x13_P2.54mm_Vertical; Mouser 200-SSQ11303TD
Y1: Crystal_GND24; Crystal_SMD_Abracon_ABM3B-4Pin_5.0x3.2mm; Mouser 520-80-10-30B-CWNT

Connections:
+5V: C21.1, C22.1, C28.1, J6.2, JP2.2, U1.20 (VCC), U7.6 (VFB), U7.7 (VOUT), U8.2 (+5V), U8.26 (+5V)
+12V: C17.1, C18.1, C27.1, D6.1 (K), J6.3, R16.1, U8.3 (+12V), U8.23 (+12V)
/BLINK: R4.1, U3.11 (AN5/C1IN1+/RPI37/RB5)
/C1RX: U2.4 (RX), U3.63 (AN27PWM2H/PMD3/RPI83/RE3)
/C1TX: U2.1 (TX), U3.64 (AN28/PWM3L/PMD4/RP84/RE4)
/CAN_H: J3.1, R11.2, R18.2, U2.7 (CANH)
/CAN_L: J3.2, R11.1, R18.1, U2.6 (CANL)
/CLK: J3.4, J5.3, JP1.2, U3.62 (AN26/PWM2L/PMD2/RP82/RE2)
/CLK_IN: C8.2, JP1.1, R7.2, U3.39 (OSC1/RPI60/RC12), Y1.1
/D0: U3.54 (C3IN2-/RP70/RD6), U8.19 (D0)
/D1: U3.55 (C3IN1+/RP71/RD7), U8.22 (D1)
/D2: U3.58 (RP96/RF0), U8.21 (D2)
/D+: J1.3 (D+), P1.A6 (D+), U1.15 (USBD+)
/D-: J1.2 (D-), P1.A7 (D-), U1.16 (USBD-)
/E1: J5.4, U3.61 (AN25/PWM1H/PMD1/RPI81/RE1)
/E2: J5.5, U3.60 (AN24/PWM1L/PMD0/RP80/RE0)
/E3: J5.6, U3.59 (RP97/RF1)
/EN: R8.2, U4.5 (EN)
/ERR: R5.1, U3.12 (AN4/C1IN2-/RPI36/RB4)
/ETH_IO: J3.3, U3.46 (INT0/RP64/RD0)
/GP6: U3.21 (AN8/PMA6/RPI40/RB8), U5.13 (~RESET)
/MCU_RXD: U1.1 (TXD), U3.5 (C1IN1-/SDI2/PMA4/RPI119/RG7)
/MCU_TXD: U1.5 (RXD), U3.3 (AN31/PWM4H/PMD7/RP87/RE7)
/MCU_~CTS: U1.3 (RTS), U3.2 (AN30/PWM4L/PMD6/RPI86/RE6)
/MCU_~RTS: U1.11 (CTS), U3.1 (AN29/PWM3H/PMD5/RP85/RE5)
/PGC: J2.5, U3.17 (PGEC1/AN6/RPI38/RB6)
/PGD: J2.4, U3.18 (PGED1/AN7/RPI39/RB7)
/PGM: J2.6
/SCK1: U3.35 (RP102/RF6), U8.9 (SCK)
/SCK2: J4.2, U3.6 (C2IN3-/SDO2/PMA3/RP120/RG8)
/SCL1: R15.2, U3.37 (SCL1/RG2), U5.14 (SCL), U8.18 (SCL1)
/SCL2: J4.10, R13.2, U3.32 (SCL2/PMA8/RP101/RF5), U8.6 (SCL2)
/SDA1: R14.2, U3.36 (SDA1/RG3), U5.15 (SDA), U8.17 (SDA1)
/SDA2: J4.9, R12.2, U3.31 (SDA2/PMA9/RP100/RF4), U8.5 (SDA2)
/SDI1: U3.45 (PMCS1/RPI75/RD11), U8.11 (SDI)
/SDI2: J4.4, U3.22 (AN9/PMA7/RPI41/RB9)
/SDO1: U3.49 (RP65/RD1), U8.10 (SDO)
/SDO2: J4.3, U3.4 (C1IN3-/SCK2/PMA5/RP118/RG6)
/SYNC: U3.53 (PMRD/RP69/RD5), U8.20 (SYNC)
/U1RX: J7.2, U3.44 (ASCL1/PMCS2/RPI74/RD10)
/U1TX: J7.3, U3.34 (RP98/RF2)
/V_USBC: D1.2 (A), J1.1 (VBUS), P1.A4 (VBUS), P1.A9 (VBUS), P1.B4 (VBUS), P1.B9 (VBUS)
/~CS1: U3.50 (RP66/RD2), U8.12 (~CS1)
/~CS2: U3.52 (PWMR/RP68/RD4), U8.13 (~CS2)
/~CS2_1: J4.5, U3.23 (TMS/AN10/PMA13/RPI42/RB10)
/~CS2_2: J4.6, U3.24 (TDO/AN11/PMA12/RPI43/RB11)
/~CS3: U3.51 (PMBE/RP67/RD3), U8.14 (~CS3)
/~INT1: R22.2, U3.47 (PGED2/SOSCI/C3IN3-/RPI61/RC13), U8.16 (~INT1)
/~INT2: J4.8, R24.2, U3.30 (AN15/PMA0/RPI47/RB15), U8.8 (~INT2)
/~MCLR: C4.1, J2.1, R6.2, R10.2, SW2.2 (B)
/~RST1: R21.2, U3.48 (PGEC2/SOSCO/C3IN1-/T1CK/RPI62/RC14), U8.15 (~RST1)
/~RST2: J4.11, R23.2, U3.42 (RTCC/RPI72/RD8), U8.7 (~RST2)
/~RST_FTDI: R1.1, U1.19 (~RESET~)
/~U1CTS: J7.5, U3.43 (ASDA1/RPI73/RD9)
/~U1RTS: J7.4, U3.33 (RP99/RF3)
GND: C1.2, C2.1, C3.2, C4.2, C5.2, C6.2, C7.1, C8.1, C9.2, C10.2, C11.2, C12.2, C13.1, C14.2, C15.2, C16.2, C18.2, C19.2, C20.2, C21.2, C22.2, C23.2, C24.2, C25.2, C26.2, C27.2, C28.2, D2.1 (K), D3.1 (K), D4.1 (K), D5.1 (K), J1.5 (GND), J1.6 (Shield), J2.3, J3.5, J4.1, J5.2, J6.5, J7.6, P1.A1 (GND), P1.A12 (GND), P1.B1 (GND), P1.B12 (GND), P1.S1 (SHIELD), R17.2, R19.2, R20.1, SW1.1 (A), SW2.1 (A), SW3.1, SW3.2, SW3.3, SW3.4, SW3.5, SW3.6, SW3.7, SW3.8, U1.7 (GND), U1.18 (GND), U1.21 (GND), U1.25 (AGND), U1.26 (TEST), U2.2 (VSS), U2.8 (STBY), U3.9 (VSS), U3.20 (AVSS), U3.25 (VSS), U3.41 (VSS), U4.3 (GND), U4.6 (TAB), U5.8 (VSS), U6.2 (GND), U7.3 (GND), U7.4 (GND), U7.5 (AGND), U7.9 (GND), U7.10 (GND), U7.13 (GND), U8.1 (GND), U8.25 (GND), Y1.2, Y1.4
unnamed: C1.1, D1.1 (K), FB1.2
unnamed: C2.2, U1.17 (3V3OUT)
unnamed: C3.1, R2.2, SW1.2 (B)
unnamed: C6.1, U3.56 (VCAP)
unnamed: C7.2, R7.1, U3.40 (OSC2/CLKO/RC15), Y1.3
unnamed: C10.1, U4.4 (NC/FB)
unnamed: C17.2, R16.2, R17.1, U6.3 (FB)
unnamed: D2.2 (A), R3.2
unnamed: D3.2 (A), R4.2
unnamed: D4.2 (A), R5.2
unnamed: D5.2 (A), R9.2
unnamed: D6.2 (A), L1.2, U6.1 (SW)
unnamed: L2.1, U7.11 (BULX)
unnamed: L2.2, U7.8 (BOLX)
unnamed: P1.A5 (CC), R19.1
unnamed: P1.B5 (VCONN), R20.2
unnamed: R9.1, U1.23 (CBUS0)
unnamed: R10.1, U3.7 (~MCLR)
unnamed: SW3.9, U5.12 (P7)
unnamed: SW3.10, U5.11 (P6)
unnamed: SW3.11, U5.10 (P5)
unnamed: SW3.12, U5.9 (P4)
unnamed: SW3.13, U5.7 (P3)
unnamed: SW3.14, U5.6 (P2)
unnamed: SW3.15, U5.5 (P1)
unnamed: SW3.16, U5.4 (P0)
VBUS: C9.1, C16.1, C19.1, C20.1, C26.1, FB1.1, J3.6, J6.4, JP2.1, L1.1, R1.2, R8.1, U2.3 (VDD), U4.1 (IN), U6.4 (EN), U6.5 (VIN), U7.1 (AVIN), U7.2 (CE), U7.12 (PVIN)

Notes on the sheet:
CAN interface
RESET/PROGRAMMING
User IO
USB interface
Power
MCU
Address selection

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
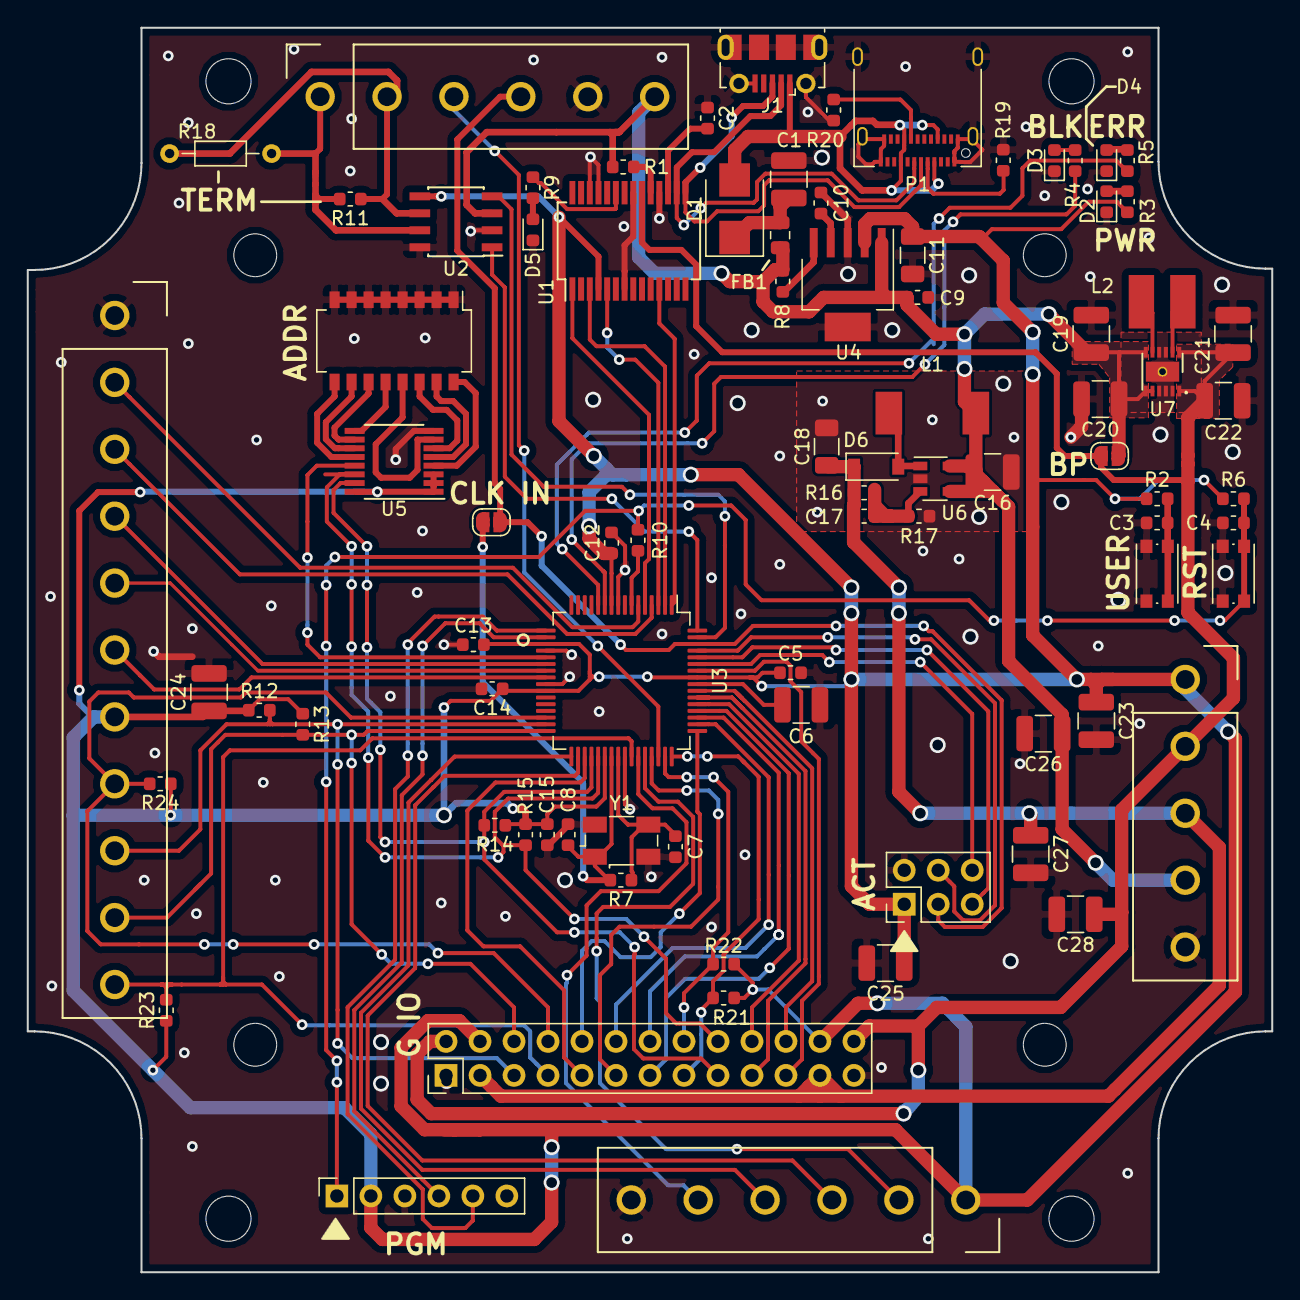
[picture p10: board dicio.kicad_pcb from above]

Board: 2 copper layers, 93.0 x 93.0 mm, 88 parts (0 on the bottom side), 83 nets.

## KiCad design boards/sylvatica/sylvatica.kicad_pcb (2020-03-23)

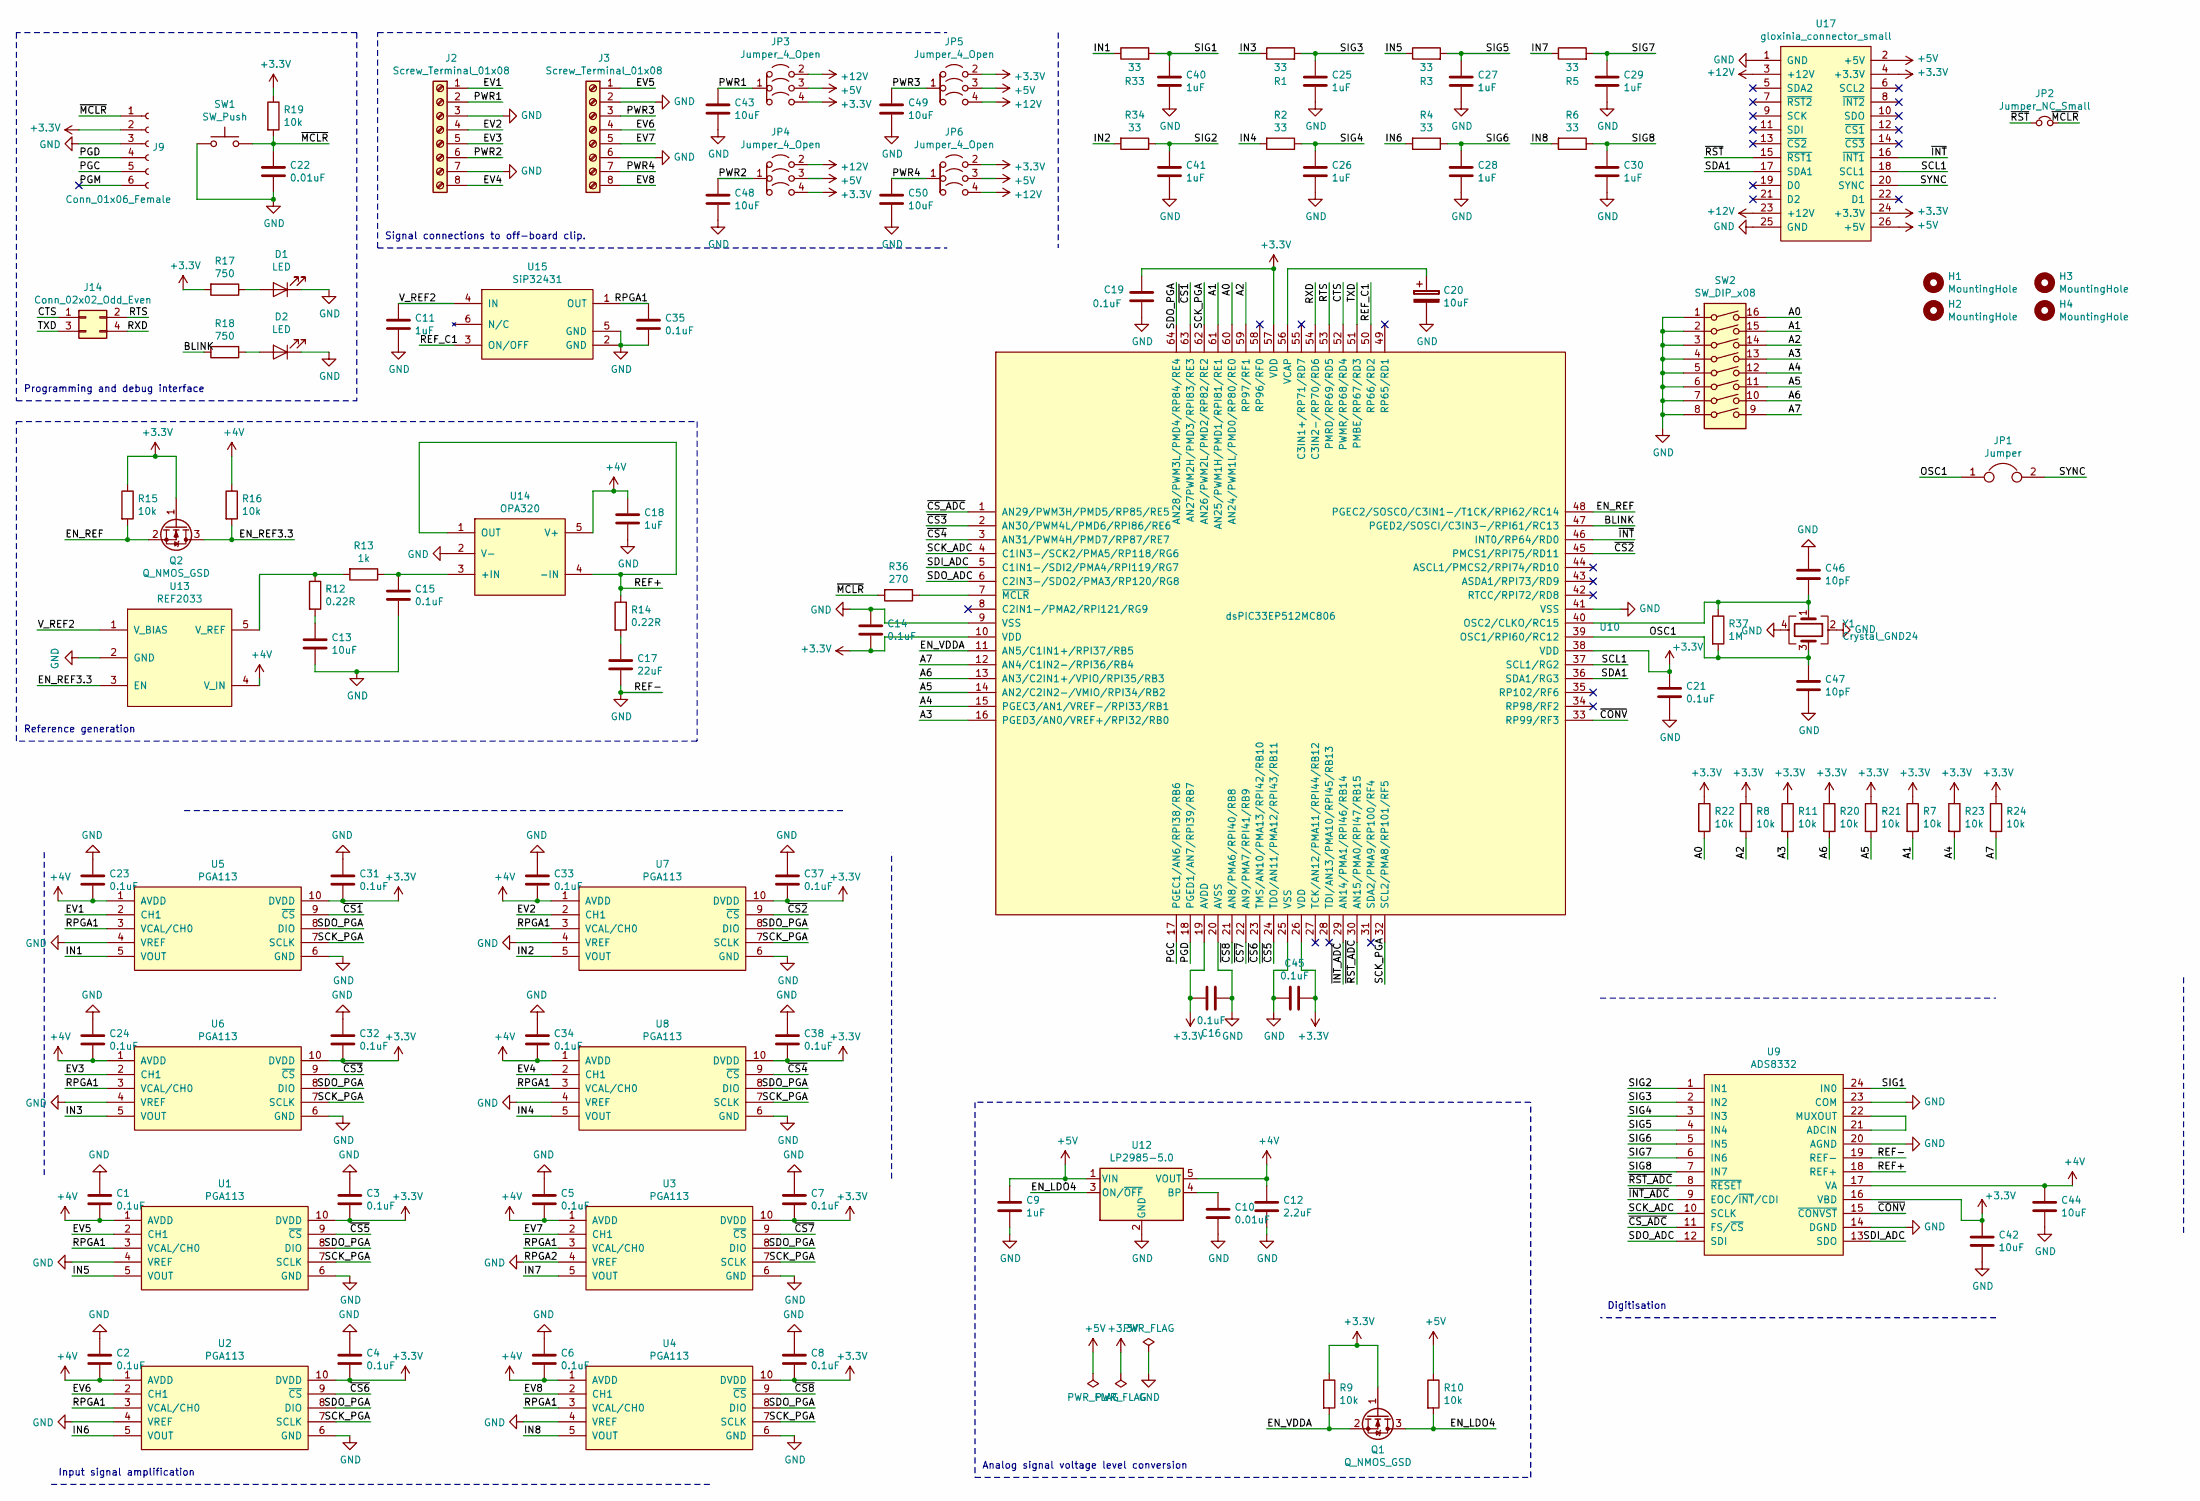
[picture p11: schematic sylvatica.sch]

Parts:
C1, C2, C3, C4, C5, C6, C7, C8, C14, C15, C16, C19, C21, C23, C24, C31, C32, C33, C34, C35, C37, C38, C45: 0.1uF; C_0603_1608Metric; Mouser 710-885012206071
C9, C11, C25, C26, C27, C28, C29, C30, C40, C41: 1uF; C_0603_1608Metric; Mouser 77-VJ0603A102GXJPBC
C10, C22: 0.01uF; C_0603_1608Metric; Mouser 77-VJ0603A102GXJPBC
C12: 2.2uF; C_1206_3216Metric; Mouser 791-1206X225K250CT
C13, C20, C42, C43, C44, C48, C49, C50: 10uF; C_1210_3225Metric; Mouser 963-TMK325BJ106KM-P
C17: 22uF; C_1206_3216Metric; Mouser 963-TMK316BBJ226ML-T
C18: 1uF; C_1210_3225Metric; Mouser 963-TMK325B7105KD-T
C46, C47: 10pF; C_0603_1608Metric; Mouser 603-CC603FRNPO9BN100
D1, D2: LED; LED_0603_1608Metric; Mouser 78-TLMS1000
H1, H2, H3, H4: MountingHole; MountingHole_3.2mm_M3
J2, J3: Screw_Terminal_01x08; TB001-500-08; Mouser 490-TB003-500-P08BE
J9: Conn_01x06_Female; PinSocket_1x06_P2.54mm_Vertical
J14: Conn_02x02_Odd_Even; PinSocket_2x02_P2.54mm_Vertical
JP1: Jumper; SolderJumper-2_P1.3mm_Open_Pad1.0x1.5mm
JP2: Jumper_NC_Small; SolderJumper-2_P1.3mm_Open_RoundedPad1.0x1.5mm
JP3, JP4, JP5, JP6: Jumper_4_Open; SolderJumper-4_Open_Pad1.0x1.5mm
Q1, Q2: Q_NMOS_GSD; SOT-23; Mouser 512-BSS138
R1, R2, R3, R4, R5, R6, R33, R34: 33; R_0603_1608Metric; Mouser 603-RC0603FR-0733RL
R7, R8, R9, R10, R11, R15, R16, R19, R20, R21, R22, R23, R24: 10k; R_0603_1608Metric; Mouser 284-APC0603B10K0N
R12, R14: 0.22R; R_0603_1608Metric; Mouser 667-ERJ-3RQFR22V
R13: 1k; R_0603_1608Metric; Mouser 652-CR0603-FX1001HLF
R17, R18: 750; R_0603_1608Metric; Mouser 603-RC0603FR-07750RL
R36: 270; R_0603_1608Metric; Mouser 603-RC0603FR-07270RL
R37: 1M; R_0603_1608Metric; Mouser 603-RC0603FR-101ML
SW1: SW_Push; SW_SPST_KMR2; Mouser 611-KMR621NGLFS
SW2: SW_DIP_x08; SW_DIP_SPSTx08_Slide_Omron_A6H-8101_W6.15mm_P1.27mm; Mouser 653-A6H-8101
U1, U2, U3, U4, U5, U6, U7, U8: PGA113; MSOP-10_3x3mm_P0.5mm; Mouser 595-PGA113AIDGSR
U9: ADS8332; TSSOP-24_4.4x7.8mm_P0.65mm; Mouser 595-ADS8332IBPWR
U10: dsPIC33EP512MC806; TQFP-64_10x10mm_P0.5mm; Mouser 579-33EP512MC806IPT
U12: LP2985-5.0; SOT-23-5; Mouser 926-LP2985IM540NOPB
U13: REF2033; SOT-23-5; Mouser 595-REF2033AIDDCR
U14: OPA320; SOT-23-5; Mouser 595-OPA320AIDBVR
U15: SiP32431; SOT-363_SC-70-6; Mouser 781-SIP32431DR3-GE3
U17: gloxinia_connector_small; PinHeader_2x13_P2.54mm_Vertical; Mouser 200-SSQ11303TD
Y1: Crystal_GND24; Crystal_SMD_Abracon_ABM3B-4Pin_5.0x3.2mm; Mouser 520-80-10-30B-CWNT

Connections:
+3V3: C3.2, C4.2, C7.2, C8.2, C14.2, C16.1, C19.1, C21.1, C31.2, C32.2, C37.2, C38.2, C42.1, C45.1, J9.2, JP3.4 (B), JP4.4 (B), JP5.2 (B), JP6.2 (B), Q1.1 (G), Q2.1 (G), R7.1, R8.1, R9.1, R11.1, R15.1, R17.2, R19.1, R20.1, R21.1, R22.1, R23.1, R24.1, U1.10 (DVDD), U2.10 (DVDD), U3.10 (DVDD), U4.10 (DVDD), U5.10 (DVDD), U6.10 (DVDD), U7.10 (DVDD), U8.10 (DVDD), U9.16 (VBD), U10.10 (VDD), U10.19 (AVDD), U10.26 (VDD), U10.38 (VDD), U10.57 (VDD), U17.4 (+3.3V), U17.24 (+3.3V)
+4V: C1.2, C2.2, C5.2, C6.2, C12.1, C18.1, C23.2, C24.2, C33.2, C34.2, C44.1, R16.1, U1.1 (AVDD), U2.1 (AVDD), U3.1 (AVDD), U4.1 (AVDD), U5.1 (AVDD), U6.1 (AVDD), U7.1 (AVDD), U8.1 (AVDD), U9.17 (VA), U12.5 (VOUT), U13.4 (V_IN), U14.5 (V+)
+5V: C9.1, JP3.3 (B), JP4.3 (B), JP5.3 (B), JP6.3 (B), R10.1, U12.1 (VIN), U17.2 (+5V), U17.26 (+5V)
+12V: JP3.2 (B), JP4.2 (B), JP5.4 (B), JP6.4 (B), U17.3 (+12V), U17.23 (+12V)
/A0: R22.2, SW2.16, U10.60 (AN24/PWM1L/PMD0/RP80/RE0)
/A1: R7.2, SW2.15, U10.61 (AN25/PWM1H/PMD1/RPI81/RE1)
/A2: R8.2, SW2.14, U10.59 (RP97/RF1)
/A3: R11.2, SW2.13, U10.16 (PGED3/AN0/VREF+/RPI32/RB0)
/A4: R23.2, SW2.12, U10.15 (PGEC3/AN1/VREF-/RPI33/RB1)
/A5: R21.2, SW2.11, U10.14 (AN2/C2IN2-/VMIO/RPI34/RB2)
/A6: R20.2, SW2.10, U10.13 (AN3/C2IN1+/VPIO/RPI35/RB3)
/A7: R24.2, SW2.9, U10.12 (AN4/C1IN2-/RPI36/RB4)
/BLINK: R18.2, U10.47 (PGED2/SOSCI/C3IN3-/RPI61/RC13)
/CTS: J14.1, U10.52 (PWMR/RP68/RD4)
/EN_LDO4: Q1.3 (D), R10.2, U12.3 (ON/~OFF~)
/EN_REF: Q2.2 (S), R15.2, U10.48 (PGEC2/SOSCO/C3IN1-/T1CK/RPI62/RC14)
/EN_REF3.3: Q2.3 (D), R16.2, U13.3 (EN)
/EN_VDDA: Q1.2 (S), R9.2, U10.11 (AN5/C1IN1+/RPI37/RB5)
/EV1: J2.1, U5.2 (CH1)
/EV2: J2.4, U7.2 (CH1)
/EV3: J2.5, U6.2 (CH1)
/EV4: J2.8, U8.2 (CH1)
/EV5: J3.1, U1.2 (CH1)
/EV6: J3.4, U2.2 (CH1)
/EV7: J3.5, U3.2 (CH1)
/EV8: J3.8, U4.2 (CH1)
/IN1: R33.1, U5.5 (VOUT)
/IN2: R34.2, U7.5 (VOUT)
/IN3: R1.1, U6.5 (VOUT)
/IN4: R2.2, U8.5 (VOUT)
/IN5: R3.1, U1.5 (VOUT)
/IN6: R4.2, U2.5 (VOUT)
/IN7: R5.1, U3.5 (VOUT)
/IN8: R6.2, U4.5 (VOUT)
/OSC1: C47.1, JP1.1, R37.2, U10.39 (OSC1/RPI60/RC12), Y1.3
/PGC: J9.5, U10.17 (PGEC1/AN6/RPI38/RB6)
/PGD: J9.4, U10.18 (PGED1/AN7/RPI39/RB7)
/PGM: J9.6
/PWR1: C43.1, J2.2, JP3.1 (A)
/PWR2: C48.1, J2.6, JP4.1 (A)
/PWR3: C49.1, J3.3, JP5.1 (A)
/PWR4: C50.1, J3.7, JP6.1 (A)
/REF+: R14.1, U9.18 (REF+), U14.1 (OUT), U14.4 (-IN)
/REF_C1: U10.50 (RP66/RD2), U15.3 (ON/OFF)
/RPGA1: C35.1, U1.3 (VCAL/CH0), U2.3 (VCAL/CH0), U3.3 (VCAL/CH0), U4.3 (VCAL/CH0), U5.3 (VCAL/CH0), U6.3 (VCAL/CH0), U7.3 (VCAL/CH0), U8.3 (VCAL/CH0), U15.1 (OUT)
/RTS: J14.2, U10.53 (PMRD/RP69/RD5)
/RXD: J14.4, U10.54 (C3IN2-/RP70/RD6)
/SCK_ADC: U9.10 (SCLK), U10.4 (C1IN3-/SCK2/PMA5/RP118/RG6)
/SCK_PGA: U1.7 (SCLK), U2.7 (SCLK), U3.7 (SCLK), U4.7 (SCLK), U5.7 (SCLK), U6.7 (SCLK), U7.7 (SCLK), U8.7 (SCLK), U10.32 (SCL2/PMA8/RP101/RF5), U10.62 (AN26/PWM2L/PMD2/RP82/RE2)
/SCL1: U10.37 (SCL1/RG2), U17.18 (SCL1)
/SDA1: U10.36 (SDA1/RG3), U17.17 (SDA1)
/SDI_ADC: U9.13 (SDO), U10.5 (C1IN1-/SDI2/PMA4/RPI119/RG7)
/SDO_ADC: U9.12 (SDI), U10.6 (C2IN3-/SDO2/PMA3/RP120/RG8)
/SDO_PGA: U1.8 (DIO), U2.8 (DIO), U3.8 (DIO), U4.8 (DIO), U5.8 (DIO), U6.8 (DIO), U7.8 (DIO), U8.8 (DIO), U10.64 (AN28/PWM3L/PMD4/RP84/RE4)
/SIG1: C40.1, R33.2, U9.24 (IN0)
/SIG2: C41.1, R34.1, U9.1 (IN1)
/SIG3: C25.1, R1.2, U9.2 (IN2)
/SIG4: C26.1, R2.1, U9.3 (IN3)
/SIG5: C27.1, R3.2, U9.4 (IN4)
/SIG6: C28.1, R4.1, U9.5 (IN5)
/SIG7: C29.1, R5.2, U9.6 (IN6)
/SIG8: C30.1, R6.1, U9.7 (IN7)
/SYNC: JP1.2, U17.20 (SYNC)
/TXD: J14.3, U10.51 (PMBE/RP67/RD3)
/V_REF2: C11.1, U13.1 (V_BIAS), U15.4 (IN)
/~CONV: U9.15 (~CONVST), U10.33 (RP99/RF3)
/~CS1: U5.9 (~CS), U10.63 (AN27PWM2H/PMD3/RPI83/RE3)
/~CS2: U7.9 (~CS), U10.45 (PMCS1/RPI75/RD11)
/~CS3: U6.9 (~CS), U10.2 (AN30/PWM4L/PMD6/RPI86/RE6)
/~CS4: U8.9 (~CS), U10.3 (AN31/PWM4H/PMD7/RP87/RE7)
/~CS5: U1.9 (~CS), U10.24 (TDO/AN11/PMA12/RPI43/RB11)
/~CS6: U2.9 (~CS), U10.23 (TMS/AN10/PMA13/RPI42/RB10)
/~CS7: U3.9 (~CS), U10.22 (AN9/PMA7/RPI41/RB9)
/~CS8: U4.9 (~CS), U10.21 (AN8/PMA6/RPI40/RB8)
/~CS_ADC: U9.11 (FS/~CS), U10.1 (AN29/PWM3H/PMD5/RP85/RE5)
/~INT: U10.46 (INT0/RP64/RD0), U17.16 (~INT1)
/~INT_ADC: U9.9 (EOC/~INT~/CDI), U10.29 (AN14/PMA1/RPI46/RB14)
/~MCLR: C22.1, J9.1, JP2.2, R19.2, R36.2, SW1.2
/~RST: JP2.1, U17.15 (~RST1)
/~RST_ADC: U9.8 (~RESET), U10.30 (AN15/PMA0/RPI47/RB15)
GND: C1.1, C2.1, C3.1, C4.1, C5.1, C6.1, C7.1, C8.1, C9.2, C10.2, C11.2, C12.2, C13.2, C14.1, C15.2, C16.2, C17.2, C18.2, C19.2, C20.2, C21.2, C22.2, C23.1, C24.1, C25.2, C26.2, C27.2, C28.2, C29.2, C30.2, C31.1, C32.1, C33.1, C34.1, C35.2, C37.1, C38.1, C40.2, C41.2, C42.2, C43.2, C44.2, C45.2, C46.1, C47.2, C48.2, C49.2, C50.2, D1.1 (K), D2.1 (K), J2.3, J2.7, J3.2, J3.6, J9.3, SW1.1, SW2.1, SW2.2, SW2.3, SW2.4, SW2.5, SW2.6, SW2.7, SW2.8, U1.4 (VREF), U1.6 (GND), U2.4 (VREF), U2.6 (GND), U3.4 (VREF), U3.6 (GND), U4.4 (VREF), U4.6 (GND), U5.4 (VREF), U5.6 (GND), U6.4 (VREF), U6.6 (GND), U7.4 (VREF), U7.6 (GND), U8.4 (VREF), U8.6 (GND), U9.14 (DGND), U9.19 (REF-), U9.20 (AGND), U9.23 (COM), U10.9 (VSS), U10.20 (AVSS), U10.25 (VSS), U10.41 (VSS), U12.2 (GND), U13.2 (GND), U14.2 (V-), U15.2 (GND), U15.5 (GND), U17.1 (GND), U17.25 (GND), Y1.2, Y1.4
unnamed: C10.1, U12.4 (BP)
unnamed: C13.1, R12.2
unnamed: C15.1, R13.1, U14.3 (+IN)
unnamed: C17.1, R14.2
unnamed: C20.1, U10.56 (VCAP)
unnamed: C46.2, R37.1, U10.40 (OSC2/CLKO/RC15), Y1.1
unnamed: D1.2 (A), R17.1
unnamed: D2.2 (A), R18.1
unnamed: R12.1, R13.2, U13.5 (V_REF)
unnamed: R36.1, U10.7 (~MCLR)
unnamed: U9.21 (ADCIN), U9.22 (MUXOUT)

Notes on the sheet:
Signal connections to off-board clip.
Programming and debug interface
Input signal amplification
Reference generation
Analog signal voltage level conversion
Digitisation

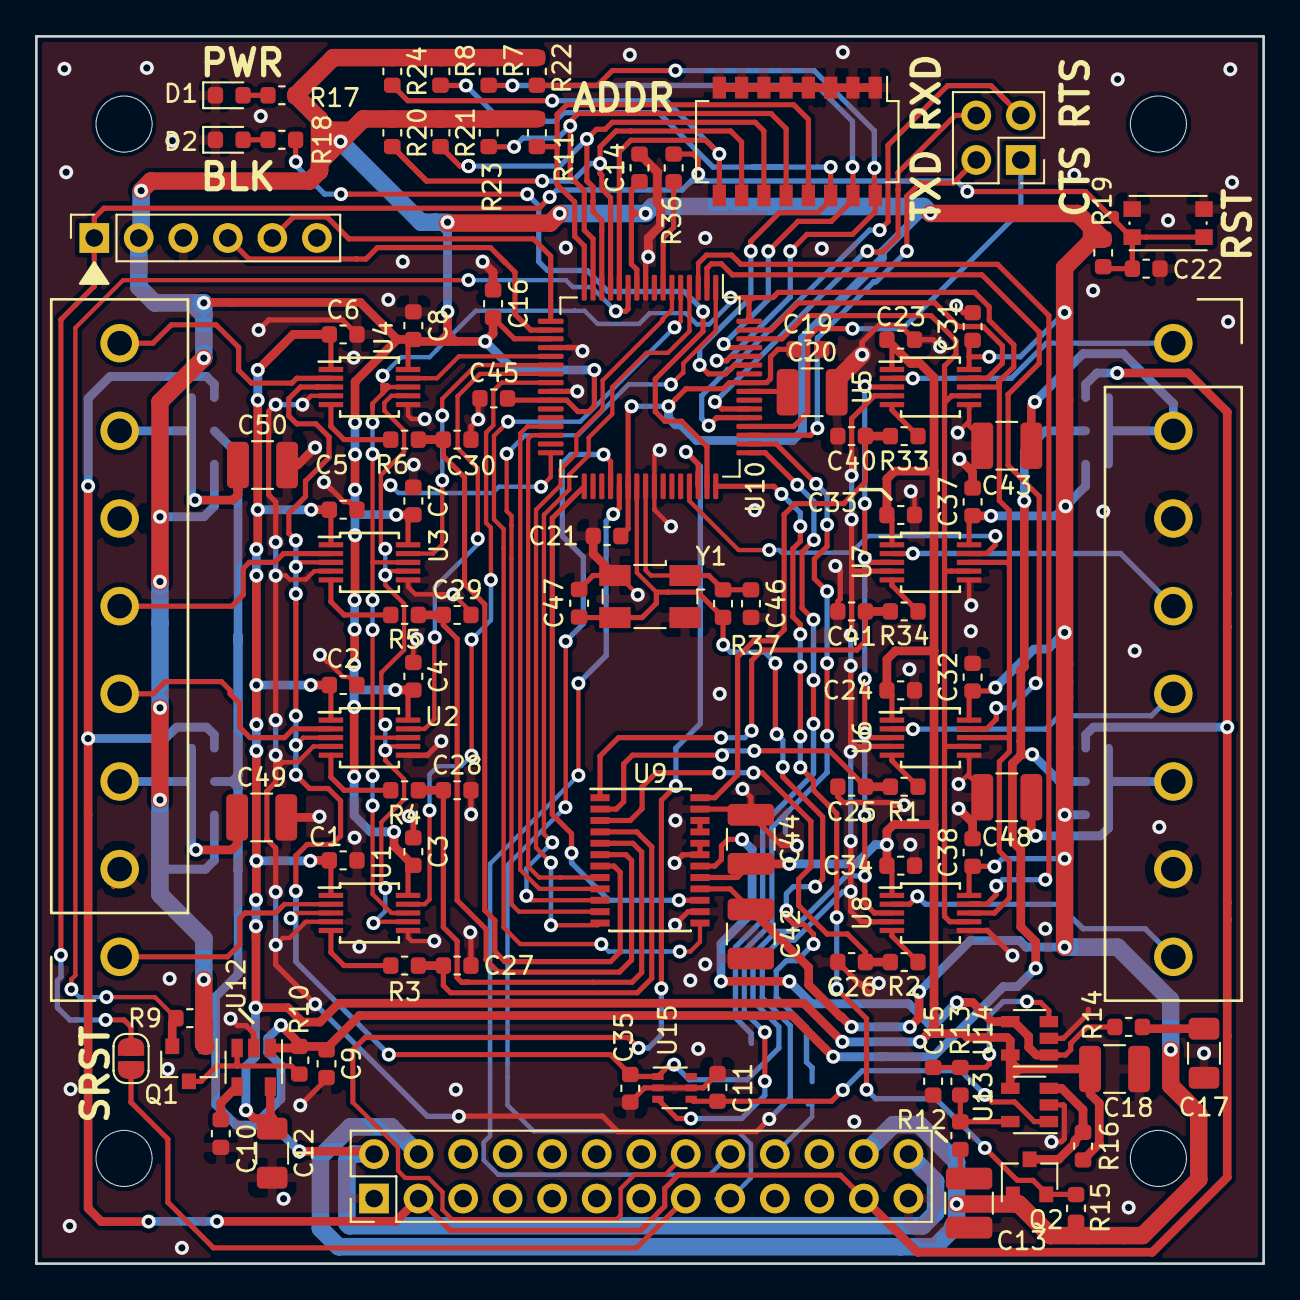
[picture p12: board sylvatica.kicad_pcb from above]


Board: 2 copper layers, 70.0 x 70.0 mm, 112 parts (5 on the bottom side), 91 nets.

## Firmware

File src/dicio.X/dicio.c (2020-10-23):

#include "dicio.h"
#include <spi.h>
#include <string.h>
#include <stdio.h>
#include <uart.h>
#include "address.h"
#include <device_configuration.h>
#include <can.h>
#include "sensors.h"
#include "actuators.h"

#define BRGVAL      ( (FCY / BAUDRATE) / 16 ) - 1
#define DICIO_BLINKY_PIN PIN_INIT(B, 5)
#define DICIO_ERROR_PIN PIN_INIT(B, 4)

#define SS1_PIN1 PIN_INIT(D, 2)
#define SS1_PIN2 PIN_INIT(D, 4)
#define SS1_PIN3 PIN_INIT(D, 3)

#define SS2_PIN1 PIN_INIT(B, 10)
#define SS2_PIN2 PIN_INIT(B, 11)

#define RST1_SENSOR_PIN PIN_INIT(C, 14)
#define RST2_SENSOR_PIN PIN_INIT(D, 8)

#define DICIO_I2C1_CONFIG {\
    .i2c_address = 0x0,\
    .status = I2C_STATUS_MASTER_ON,\
    .mw_sr_cb = dicio_i2c_mw_sr_callback,\
    .mr_sw_cb = dicio_i2c_mr_sw_callback,\
    .scl_pin = PIN_INIT(G, 2),\
    .sda_pin = PIN_INIT(G, 3)}

#define DICIO_I2C2_CONFIG {\
    .i2c_address = 0x0,\
    .status = I2C_STATUS_MASTER_ON,\
    .mw_sr_cb = dicio_i2c_mw_sr_callback,\
    .mr_sw_cb = dicio_i2c_mr_sw_callback,\
    .scl_pin = PIN_INIT(F, 5),\
    .sda_pin = PIN_INIT(F, 4)}

static dicio_config_t config = {
    .blinky_pin = DICIO_BLINKY_PIN,
    .error_pin = DICIO_ERROR_PIN,
    .rst1_sensor_pin = RST1_SENSOR_PIN,
    .rst2_sensor_pin = RST2_SENSOR_PIN,
    .spi1_ss = {SS1_PIN1, SS1_PIN2, SS1_PIN3},
    .spi2_ss = {SS2_PIN1, SS2_PIN2},
    .i2c_config = {DICIO_I2C1_CONFIG, DICIO_I2C2_CONFIG},
    .output_frequency = 8000000,
};

int16_t n_connected_can_devices;

static void (*__sensor_timer_callback)(void) = dicio_dummy_callback;
static void (*__actuator_timer_callback)(void) = dicio_dummy_callback;

void dicio_dummy_callback(void){
    
}

void dicio_set_sensor_callback(void (*cb)(void)){
    __sensor_timer_callback = cb;
}

void dicio_set_actuator_callback(void (*cb)(void)){
    __actuator_timer_callback = cb;
}

void init_sample_timer(void){
    T9CONbits.TON = 0;
    T9CONbits.TCS = 0; // use internal instruction cycle as clock source
    T9CONbits.TGATE = 0; // disable gated timer
    T9CONbits.TCKPS = 0b11; // prescaler 1:256
    TMR9 = 0; // clear timer register
    PR9 = (uint16_t) ((FCY / 256) / DICIO_READ_FREQUENCY) - 1; // set period
    _T9IF = 0; // clear interrupt flag
    _T9IE = 1; // enable interrupt
    
    // start timer 
    T9CONbits.TON = 1;
}

void init_sample_detection(void){
    // start timer 
    _INT0EP = 0; // interrupt on the positive edge
    
    _INT0IF = 0; // clear interrupt flag
    _INT0IE = 1; // enable interrupt
}

void __attribute__ ( (__interrupt__, no_auto_psv) ) _T9Interrupt( void ){
    __sensor_timer_callback();
    __actuator_timer_callback();
    _T9IF = 0;
}

void __attribute__ ( (__interrupt__, no_auto_psv) ) _INT0Interrupt( void ){
    __sensor_timer_callback();
    __actuator_timer_callback();
    _INT0IF = 0;
}

void dicio_init_pins(void){
    // I2C1 pins
    // pin configuration
    
    _TRISG2 = 0;
    _TRISG3 = 0;
    _LATG2 = 1;
    _LATG3 = 0;
    delay_ms(1);
    _LATG2 = 1;
    _LATG3 = 1;
    delay_ms(1);
    _ODCG2 = 1;  // configure I2C pins as open drain output
    _ODCG3 = 1; // configure I2C pins as open drain outputs
    
    
    _ANSC13 = 0; // configure nINT1 as digital pin
    _TRISC13 = 1; // configure nINT1 as digital input pin    
    //_ANSC14 = 0; // configure nRST1 as digital pin
    //_TRISC14 = 1; // configure nRST1 as digital output pin   
    //_LATC14 = 1;
    _ANSB8 = 0;  // dedicated reset to address selector
    _TRISB8 = 0;
    _LATB8 = 1;
    
    // I2C2 pins
    _TRISF4 = 0;
    _TRISF5 = 0;
    
    _LATF5 = 1;
    _LATF4 = 0;
    delay_ms(1);
    _LATF4 = 1;
    _LATF5 = 1;
    delay_ms(1);
    _ODCF4 = 1; // configure I2C pins as open drain output
    _ODCF5 = 1; // configure I2C pins as open drain output
    
    _ANSB15 = 0; // configure nINT1 as digital pin
    _TRISB15 = 1; // configure nINT2 as digital input pin 
    _ODCD8 = 1;
    _CNPUD8 = 1;
    _TRISD8 = 0; // configure nRST2 as digital output pin   
    _LATD8 = 1; 
    
    // UART to PC
    _ANSE5 = 0;            // U2 RTS
    _TRISE5 = 0;
    _RP85R = _RPOUT_U2RTS;
    _ANSE6 = 0;            // U2 CTS
    _U2CTSR = 86;
    _TRISE6 = 1;
    _ANSE7 = 0;            // U2 TX
    _TRISE7 = 0;
    _RP87R = _RPOUT_U2TX;
    _ANSG7 = 0;            // U2 RX
    _TRISG7 = 1;
    _U2RXR = 119;
    
    // UART to peripheral
    //_TRISF3 = 0;            // U1 RTS
    //_RP99R = _RPOUT_U1RTS;
    _TRISF2 = 0;            // U1 TX
    _RP98R = _RPOUT_U1TX;
    //_TRISD9 = 1;            // U1 CTS
    //_U1CTSR = 73;
    _TRISD10 = 1;           // U1 RX
    _U1RXR = 74;
    
    // UART to peripheral
    /*_TRISF3 = 0;            // U3 TX
    _RP99R = _RPOUT_U3TX;
    _TRISD9 = 1;           // U3 RX
    _U3RXR = 73;*/
    _TRISF3 = 1;
    _TRISD9 = 1;
    
    // CAN
    // ECAN pin configuration
    _ANSE4 = 0;          // CAN1 TX
    _TRISE4 = 0;
    _RP84R = _RPOUT_C1TX;
    _ANSE3 = 0;          // CAN1 RX
    _TRISE3 = 1;
    _C1RXR = 83;
    
    // SPI1 configuration   
    _TRISD11 = 1;          // SDI1 
    _SDI1R = 75;
    _TRISF6 = 0;           // SCK1
    _RP102R = _RPOUT_SCK1;
    _TRISD1 = 0;           // SDO1
    _RP65R = _RPOUT_SDO1;
    
    // SPI3 configuration
    _ANSB9 = 0; // SDI3
    _TRISB9 = 1; 
    _SDI3R = 41;
    _ANSG8 = 0; // SCK3
    _TRISG8 = 0;
    _RP120R = _RPOUT_SCK3;
    _ANSG6 = 0; // SCK3
    _TRISG6 = 0;
    _RP118R = _RPOUT_SDO3;
    
    // SYNC configuration
    _TRISD5 = 0;
    _RP69R = _RPOUT_OC1;
    _LATD5 = 0;
    
    // external pins: default config is digital input
    _ANSE2 = 0;   // E0 / CLK
    _TRISE2 = 1;
    _ANSE1 = 0;   // E1
    _TRISE1 = 1;
    _ANSE0 = 0;   // E2
    _TRISE0 = 1;
    _TRISF1 = 1;  // E3
    
    // control pins: default config is digital input 
    _ANSD6 = 0;   // D0
    _TRISD6 = 1;
    _ANSD7 = 0;   // D1
    _TRISD7 = 1;
    _TRISF0 = 1;  // D2
    
    // CAN ETH IO
    _TRISD0 = 1;
    
    // LED (BLINKY, ERROR)
    _ANSB5 = 0;
    _ANSB4 = 0;
    
    // reset sensors
    //CLEAR_BIT(config.rst_sensor_pin.tris_r, config.rst_sensor_pin.n);
    //SET_BIT(config.rst_sensor_pin.lat_r, config.rst_sensor_pin.n);
}

void detect_can_devices(void){
    can_message_t m;
    bool no_device_found = false;
    
    can_init_message(&m, controller_can_address, CAN_NO_REMOTE_FRAME, 
            CAN_EXTENDED_FRAME, CAN_HEADER(CAN_INFO_MSG_HELLO, 0), NULL, 0);
    
    can_send_message_any_ch(&m);
    
    delay_ms(100);
    
    // check CAN status
    if(C1TR01CONbits.TXREQ0 == 1){
        no_device_found = true;
    }
    if(C1TR01CONbits.TXREQ1 == 1){
        no_device_found = true;
    }
    if(C1TR23CONbits.TXREQ2 == 1){
        no_device_found = true;
    }
    if(C1TR23CONbits.TXREQ3 == 1){
        no_device_found = true;
    }
    if(C1TR45CONbits.TXREQ4 == 1){
        no_device_found = true;
    }
    if(C1TR45CONbits.TXREQ5 == 1){
        no_device_found = true;
    }
    if(C1TR67CONbits.TXREQ6 == 1){
        no_device_found = true;
    }
    if(C1TR67CONbits.TXREQ7 == 1){
        no_device_found = true;
    }
    
    // disable CAN if needed
    if(no_device_found){
        n_connected_can_devices = 0;
        
        #ifdef ENABLE_DEBUG        
        sprintf(print_buffer, "No CAN devices found.");
        uart_print(print_buffer, strlen(print_buffer));
        #endif

        can_disable();
    } else {
        n_connected_can_devices = 1;
        
        #ifdef ENABLE_DEBUG        
        sprintf(print_buffer, "At least one CAN device found.");
        uart_print(print_buffer, strlen(print_buffer));
        #endif
    }
}

void init_trigger_generation(void){
    // configure OC3 and OC4 to generate a pulse every 100ms
    OC3CON1bits.OCM = 0b000; // Disable Output Compare Module
    OC4CON1bits.OCM = 0b000; // Disable Output Compare Module
    
    // user peripheral clock as clock source
    OC3CON1bits.OCTSEL = 0b111; 
    OC4CON1bits.OCTSEL = 0b111;
    
    // Write the frequency for the PWM pulse
    uint32_t period_value = FCY / 10;
    
    OC3RS = (uint16_t) (period_value - 1);
    OC4RS = (uint16_t) ((period_value - 1) >> 16);
    
    // Write the duty cycle for the PWM pulse
    period_value /= 2;
    OC3R = (uint16_t) (period_value - 1);
    OC4R = (uint16_t) ((period_value - 1) >> 16);
    
    // no sync or trigger source
    OC3CON2bits.SYNCSEL = 0b11111; 
    OC4CON2bits.SYNCSEL = 0b11111; 
    
    // continue operation in CPU idle mode
    OC3CON1bits.OCSIDL = 0;
    OC4CON1bits.OCSIDL = 0;
    
    // synchronised mode
    OC3CON2bits.OCTRIG = 0;
    OC4CON2bits.OCTRIG = 0;
    
    // output 
    OC3CON2bits.OCTRIS = 1; // since the OC3 pin is not used, the output should be tri-stated
    
    // enable cascade operation
    OC4CON2bits.OC32 = 1; // even module must be enabled first
    OC3CON2bits.OC32 = 1;
    
    _OC3IF = 0;              // clear the OC3 interrupt flag
    _OC3IE = 0;              // disable OC3 interrupt
    _OC4IF = 0;              // clear the OC4 interrupt flag
    _OC4IE = 0;              // disable OC4 interrupt
    
    // Select the Output Compare mode: EDGE-ALIGNED PWM MODE
    OC4CON1bits.OCM = 0b110; 
    OC3CON1bits.OCM = 0b110;
}

void dicio_init(void){
    i2c_error_t i2c_error;
    
    set_error_loop_fn(i2c_process_queue);
    
    set_error_pin(&config.error_pin);
    
    #ifdef ENABLE_DEBUG        
        sprintf(print_buffer, "Initialising pins...");
        uart_print(print_buffer, strlen(print_buffer));
    #endif
    dicio_init_pins();   
    
    #ifdef ENABLE_DEBUG        
        sprintf(print_buffer, "Initialising output clock reference.");
        uart_print(print_buffer, strlen(print_buffer));
    #endif
    dicio_init_clock_sync();
    dicio_start_clock_sync();

    #ifdef ENABLE_DEBUG        
        sprintf(print_buffer, "Initialised blinky.");
        uart_print(print_buffer, strlen(print_buffer));
    #endif
    blinky_init(&config.blinky_pin, 1);
    
    #ifdef ENABLE_DEBUG        
        sprintf(print_buffer, "Initialising I2C1.");
        uart_print(print_buffer, strlen(print_buffer));
    #endif
    i2c1_init(&config.i2c_config[0]);
    
    #ifdef ENABLE_DEBUG        
        sprintf(print_buffer, "Initialising I2C2.");
        uart_print(print_buffer, strlen(print_buffer));
    #endif
    i2c2_init(&config.i2c_config[1]);
    
    #ifdef ENABLE_DEBUG        
        sprintf(print_buffer, "Initialising device address.");
        uart_print(print_buffer, strlen(print_buffer));
    #endif
    i2c_error = set_device_address();
    if(i2c_error == I2C_NO_ERROR) {
    #ifdef ENABLE_DEBUG
        sprintf(print_buffer, "Initialised device address to 0x%x.", controller_address);
        uart_print(print_buffer, strlen(print_buffer));
    #endif
    } else {
    #ifdef ENABLE_DEBUG        
        sprintf(print_buffer, "Failed to initialise device address.");
        uart_print(print_buffer, strlen(print_buffer));
    #endif
    }
    
    #ifdef ENABLE_DEBUG        
        sprintf(print_buffer, "Initialising ECAN.");
        uart_print(print_buffer, strlen(print_buffer));
    #endif
    can_init();
    
    #ifdef ENABLE_DEBUG        
        sprintf(print_buffer, "Detecting if other devices connected using CAN.");
        uart_print(print_buffer, strlen(print_buffer));
    #endif
    detect_can_devices();
    
    if(controller_address == 0){
        _TRISD0 = 0;
        _RP64R = _RPOUT_OC2;
        init_trigger_generation();
    } else {
        _TRISD0 = 1;
        init_sample_detection();
    }
}
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

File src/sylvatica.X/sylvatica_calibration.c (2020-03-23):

#include "sylvatica_calibration.h"
#include <pga.h>
#include <spi.h>
#include <adc.h>
#include <fir_common.h>
#include <math.h>
#include <uart.h>
#include <utilities.h>

extern volatile uint8_t copy_buffer_selector;
extern uint16_t copy_buffers_a[SYLVATICA_N_CHANNELS][SYLVATICA_COPY_BUFFER_SIZE];
extern uint16_t copy_buffers_b[SYLVATICA_N_CHANNELS][SYLVATICA_COPY_BUFFER_SIZE];
extern sylvatica_config_t gconfig;


void sylvatica_run_calibration(sylvatica_config_t* config){
    pga_config_t pga_backup[SYLVATICA_N_CHANNELS];
    uint16_t i;
    adc_config_t adc_config = config->adc_config;
    
    // ADC in manual mode
    adc_config.trigger_select = ADC_TRIGGER_SELECT_MANUAL;
    adc_config.channel_select = ADC_CHANNEL_SELECT_MODE_MANUAL;
    adc_config.nap_powerdown = ADC_AUTO_NAP_POWERDOWN_DISABLE;
    adc_config.deep_powerdown = ADC_DEEP_POWERDOWN_DISABLE;
    adc_config.tag_output = ADC_TAG_OUTPUT_DISABLE;
    
    // save PGA configuration and turn all PGAs off
    for(i = 0; i < SYLVATICA_N_CHANNELS; i++){
        pga_backup[i] = config->pga_config[i];
        
        config->pga_config[i].status = PGA_STATUS_OFF;
        
        update_pga_status(&config->pga_config[i]);
    }
    
    // configure ADC
    update_adc(&adc_config);
    
    delay_ms(100);
    
    
    // run calibration for each channel
    for(i = 0; i < SYLVATICA_N_CHANNELS; i++){
        // turn PGA on
        config->pga_config[i].status = PGA_STATUS_ON;
        config->pga_config[i].channel = PGA_CAL3;
        config->pga_config[i].gain = PGA_GAIN_1;
        update_pga_status(&config->pga_config[i]);
        
        // allow circuit to settle
        delay_ms(1);
        
        // select correct channel
        adc_config.channel = i;
        config->adc_config.channel_offset[i] = run_calibration(&adc_config, 0);
        
#ifdef ENABLE_DEBUG
        sprintf(print_buffer, "Calibration offset CH%d: %04x.", i, config->adc_config.channel_offset[i]);
        uart_print(print_buffer, strlen(print_buffer));
#endif
        
        // turn PGA off
        config->pga_config[i].status = PGA_STATUS_OFF;
        update_pga_status(&config->pga_config[i]);
    }
    
    
    // restore previous PGA configuration
    for(i = 0; i < SYLVATICA_N_CHANNELS; i++){
        config->pga_config[i] = pga_backup[i];
        
        update_pga_status(&config->pga_config[i]);
    }
    
    // restore ADC to previous configuration
    update_adc(&config->adc_config);
}
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
